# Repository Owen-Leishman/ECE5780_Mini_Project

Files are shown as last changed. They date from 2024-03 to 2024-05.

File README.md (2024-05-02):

# Demonstration Neural Interface
>[!warning]
>This is a demonstration device, this hardware is relatively untested and not gauranteed to be safe! This is not designed live test subjects!

## Overview
This is a demonstration neural interface which is meant to explore how neural interfaces work.  This device can measure four differential signals at a time which can be used to measure nerve impulses and are tolerant of ±9V. It also has a current mode stimulation channel which can create ±1mA signals with 9 bits of resolution as a means to give feedback to the nerves. The stimulation channel can handle electrodes with up to 9kΩ. The device also has a temperature sensor to measure how much it heats up to ensure that it would be safe if implanted (at least temperature wise). The device can be controlled over wifi, and is fully battery powered.

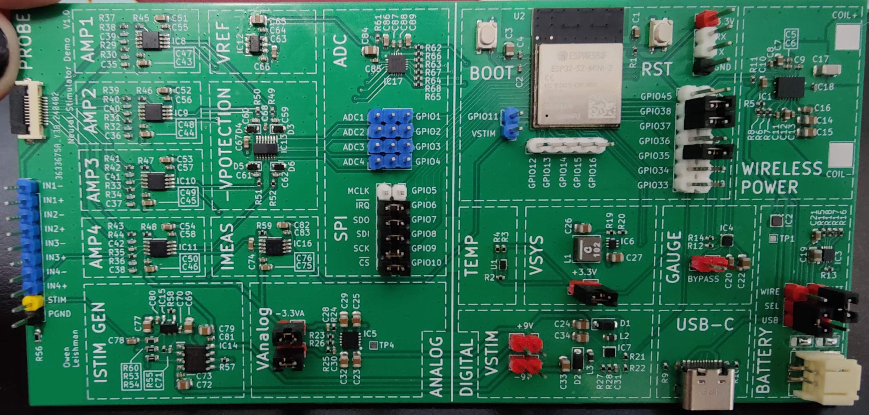
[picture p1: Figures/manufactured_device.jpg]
Manufactured device

(A logo was edited out on the bottom left corner of the device, the photo is otherwise not edited)

## Organization
- [Firmware](/Firmware/Neural_Demo/) contains the code that the device runs.
- [Hardware](/Hardware/) contains the design of the device.
- [Software](/Software/) contains the code used to interface with the device.

For information on how to use the device refer to the [software directory](/Software/).

For information on how to manufacture the device refer to the [hardware directory](/Hardware/).

## Results
The device has exceptional accuracy and can measure down to the uV using its discreate ADC.
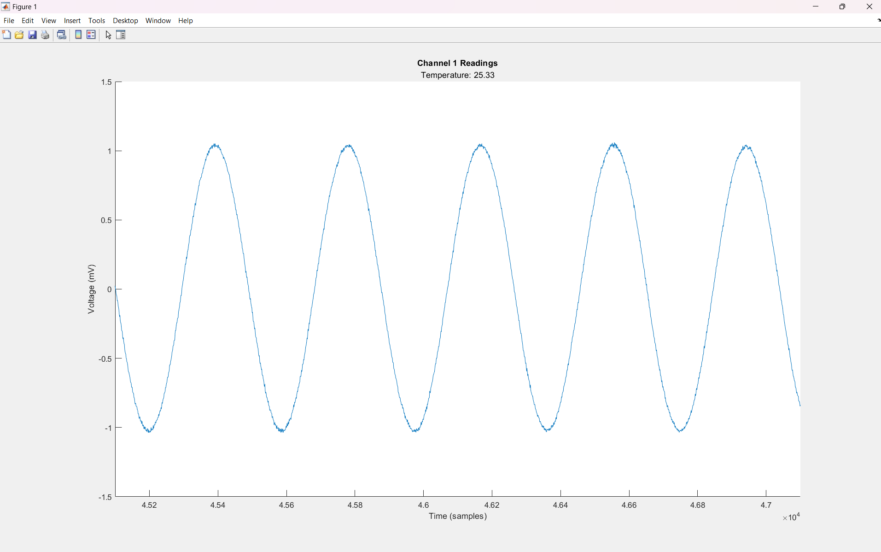
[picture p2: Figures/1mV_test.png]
Low Voltage Test

This test was run using an external signal generator to create a 1mV peak-to-peak sine wave at 500mHz. (This test was also done with old software and firmware some of the ADC configuration has been changed).

The demonstration software makes it possible to measure all four channels in real time over wifi, and the measured stimulation current. The software also makes it possible to control the amplitude and waveform the current stimulation uses.
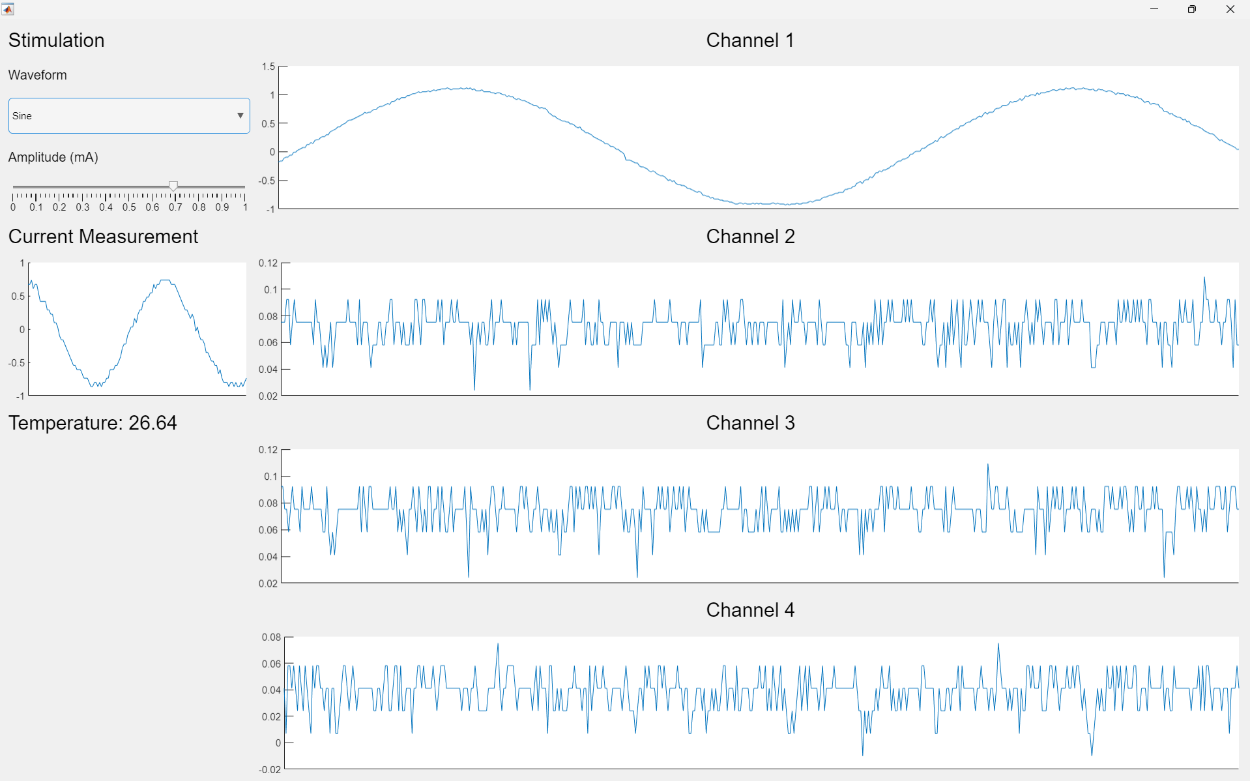
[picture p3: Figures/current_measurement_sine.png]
Full sweet

The discreate ADC broke so the ESP32's onboard ADC (which is much worse) was used for this test. An external signal generator was connected to channel 1 to create a 1V peak-to-peak sine wave, and an external load resistor was used to connect the stimulation output to ground.

# Design Overview
Here are is the top level design of the device, for detailed information on the desing refer to the [hardware directory](Hardware).

## Top Level Design
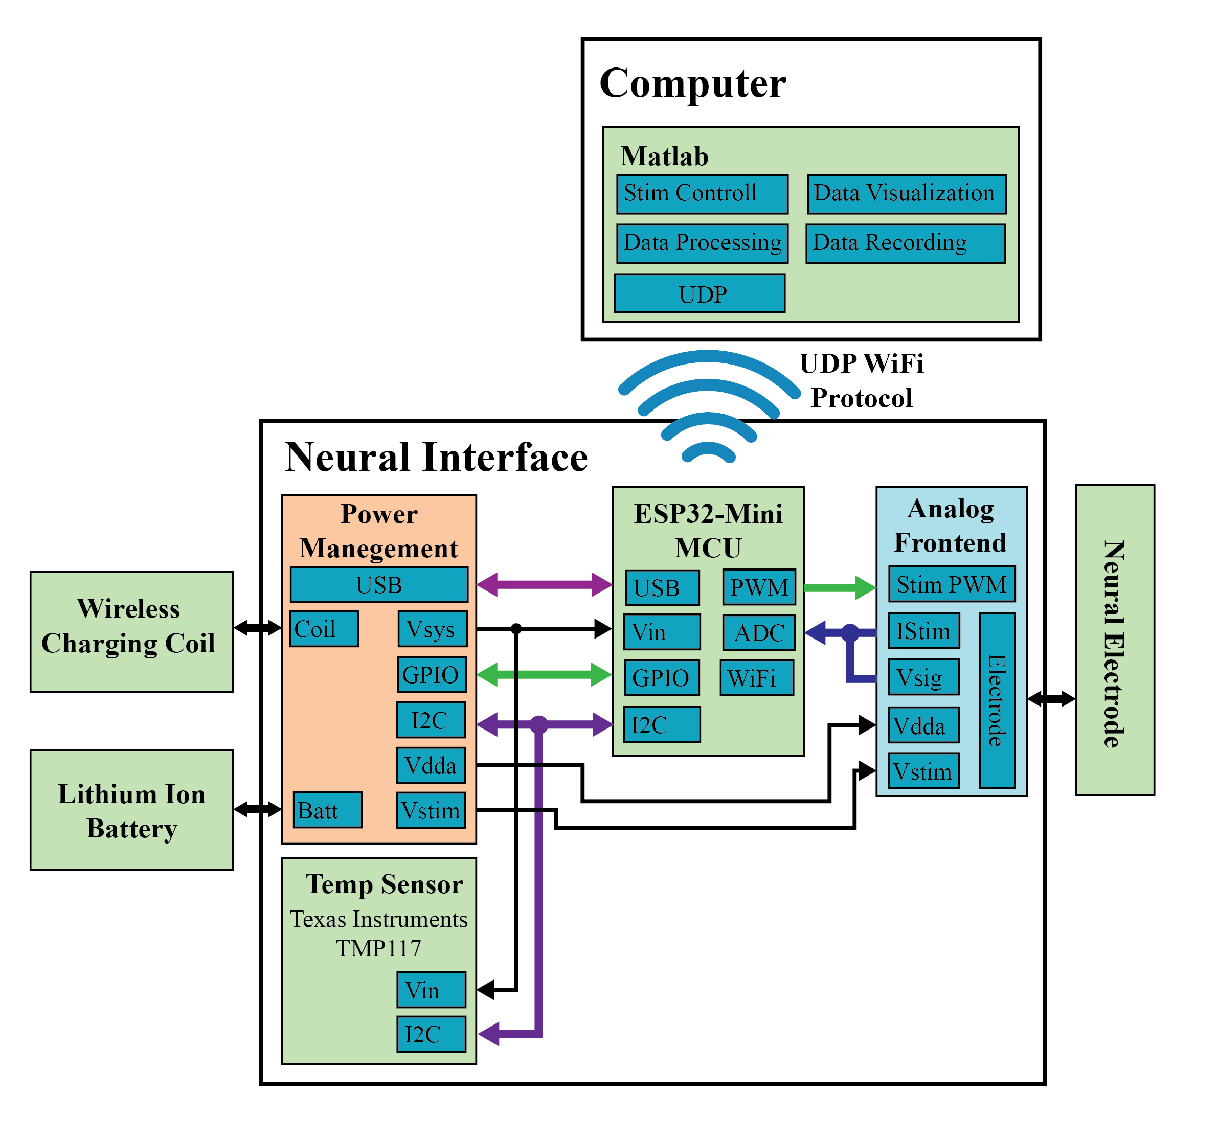
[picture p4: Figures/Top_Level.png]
Top level block diagram

The ESP32 microcontroller is used to control the whole device. The analog frontend is used to aquire data from the differential inputs, and output stimulation signals. The power distrobution block manages the battery and all of the supply voltages.

## Analog Frontend
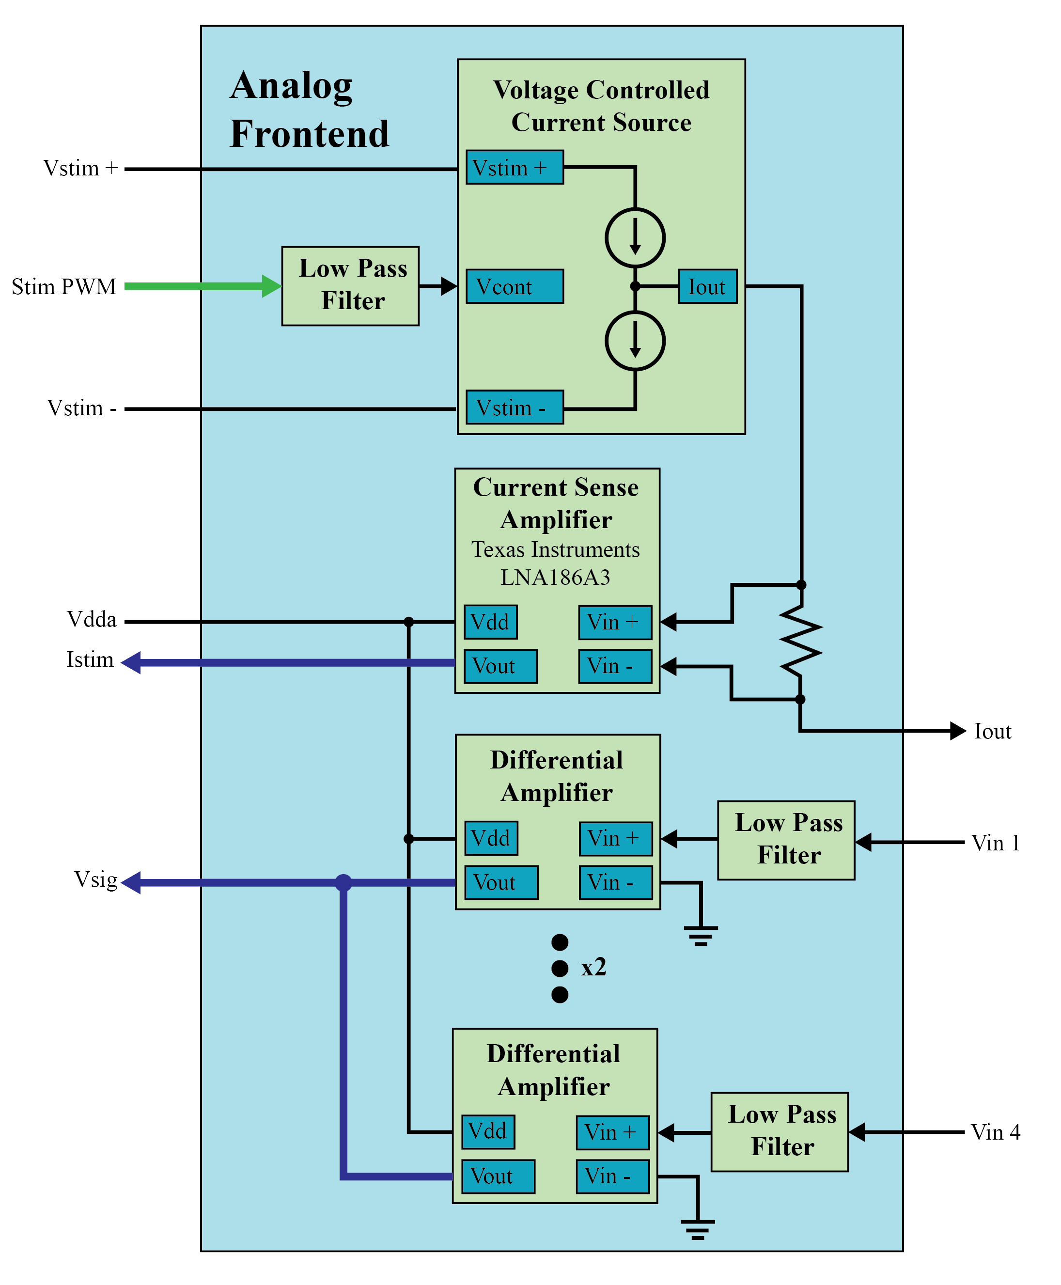
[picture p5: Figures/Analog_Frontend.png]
Analog frontend block diagram


## Power Distrobution
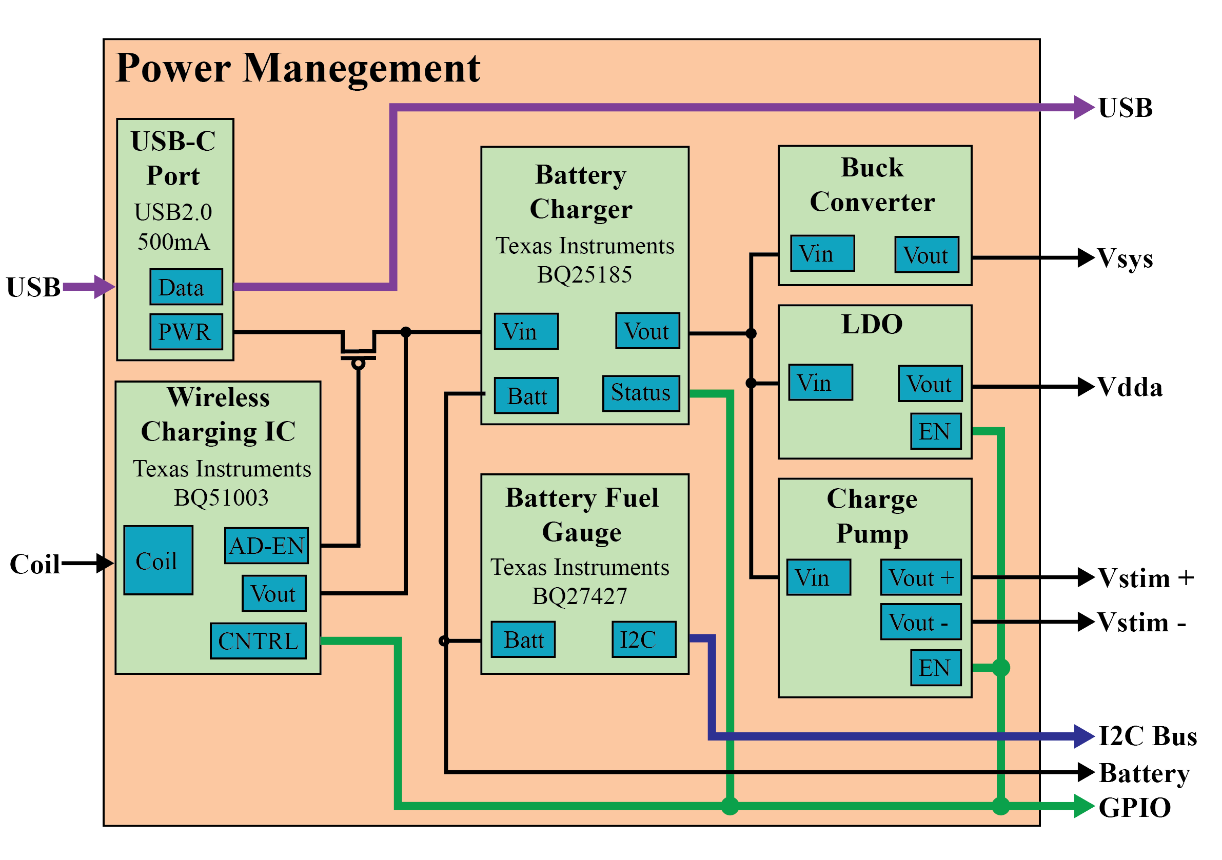
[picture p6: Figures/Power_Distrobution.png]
Power Distrobution block diagram


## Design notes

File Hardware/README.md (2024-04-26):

# Demonstration Neural Interface Hardware
>[!warning]
>This is a demonstration device, this hardware is relatively untested and not gauranteed to be safe! This is not designed live test subjects!

>[!note]
>Made with KiCad version 7.0,  [Kicad Download](https://www.kicad.org/download/)

The hardware for the demonstration neural interface.

## Tasks
- [ ] Test BQ51013BRHLR wirless power IC.
- [ ] Add voltage divider/modify signal path for onboard ADC.
- [ ] Find replacement for AD8067ARTZ operational amplifier used in the current source.
- [ ] Find issues with MCP3464 ADC (may have been ESD)

# Assembled Device
Manufactured device
>[!warning]
>This device uses BGA components and is not trivial to solder. Due to the large amount of surface mount components on the device it is recomended to use a stencil and a reflow oven for soldering.

## Current Source Fix
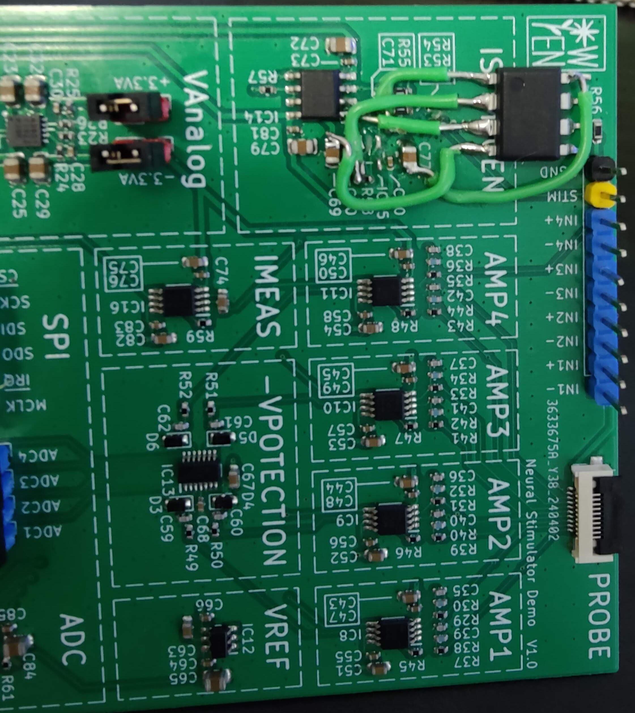
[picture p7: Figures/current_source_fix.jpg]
Current Source Fix

The AD8067ARTZ was broken (reason still unknown) so a LF353N was used to replace it for testing.

## Onboard ADC Fix
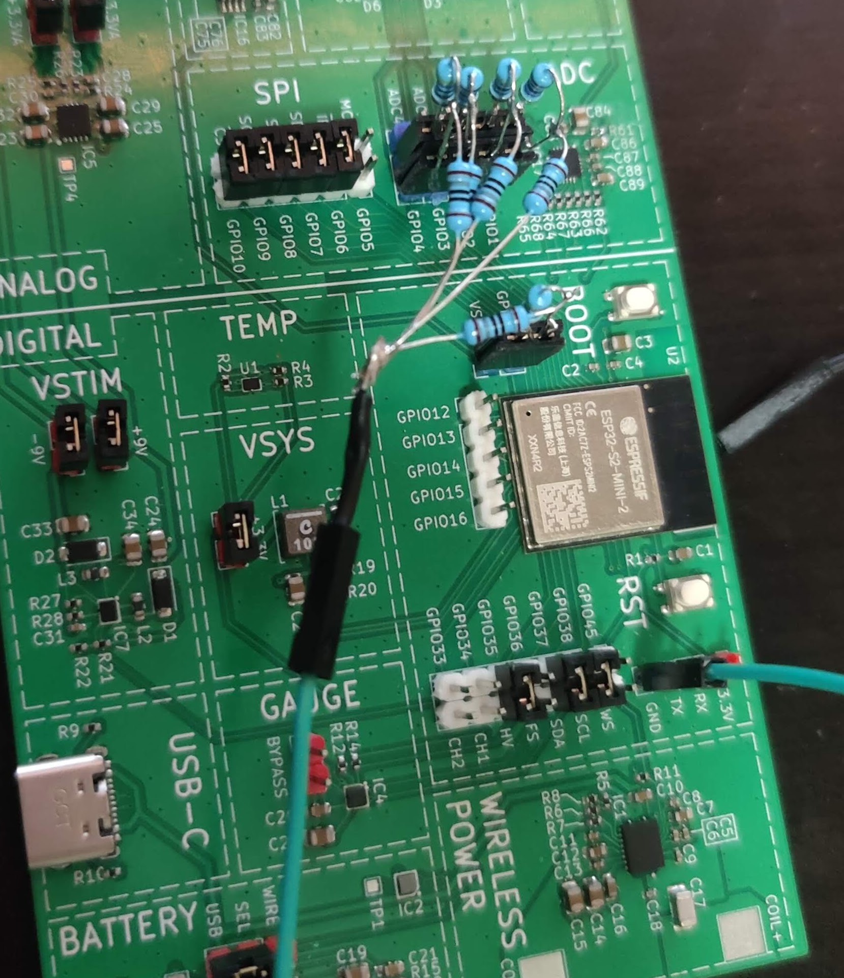
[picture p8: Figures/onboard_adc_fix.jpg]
Onboard ADC Fix

The MCP3464RT ADC broke so the ESP32's onboard ADC was used. The onboard ADC can not measure voltages larger than ~200mV so voltage dividers were added to divide all of the signals into that range, 4.7K and 180R resistors were used to create the voltage dividers. This creates a lot of noise and distortion in the signals. Due to this onboard ADC will not be used or supported in future revisions.

# Schematics
## Top Level Schematic
Top level schematic
Schematic for the ESP32 S2-mini and supporting circuitry which is used to control the device. Jumpers are added between the ESP32's gpio and board signals to make it possible to rerout signals if there is a conflict, or prevent interference for analog signals if the onboard ADC is not being used. The temperature sensor is also on this schematic.

## Analog Frontend Schematic
Analog frontend schematic
Schematic for the analog frontend used to measure "neural" signals and output current mode stimulation. The differential input signals are fed into voltage dividers to ensure that the maximum voltage that reaches the system is ±3.3V, and to create a 1MΩ input impedance. Instrumentation amplifiers are used to amplify the differential signals (satureates at ±1V but is tolerant fo ±9V) and convert them to single ended signals (0-3.3V) centered around Vref (1.6V). The outut of the instrumentation amplifiers is fed into a buffered opamp with a shotkey diode to prevent negative voltages from reaching the ADC when the instrumentation amplifiers get saturated with a negative signal (Ie. an input of -9V), this opamp will likely be removed in future revisions. Low pass filterers and decoupling capacitors are implemented throughout the design to reduce noise.

The current mode stimulation is created using an advanced howland current source implementation based on an [article by Nick Jiang from Analog Devices](https://www.analog.com/en/resources/analog-dialogue/articles/a-large-current-source-with-high-accuracy-and-fast-settling.html). The current sources is controlled by using both DACs on the ESP32, one DAC is used for creating positive currents while the other is used to create negative curents. The maximum output current is ±1mA when 3.3V is supplied by one of the DACs. The maximum probe impedance the current source can handle is 9kΩ, since the stimulation voltage is ±9V. A capacitor is added in series to the output current to prevent continous stimulation in case of a device malfunction (this capacitor was shorted to test the current source at low frequencies).

## Power Manegement Schematic
Power manegement schematic
Schematic for the power manegement circuitry which supplies power to the device and maneges the battery. The device can be powered from using wireless charging, USB type C, or the onboard battery. The BQ51013BRHLR wireless charging IC automatically selects if the BQ25185DLHR battery charging IC will be suplied with usb power or wireless power based on which one is present. The battery charging IC controlls the battery charge rate, and charge and discharge threshold and determines if the voltage regulators for the rest of the system will be supplied with battery power or the power selected by the wireless charging IC. A BQ27427YZFR is placed in series with the battery to measure battery life.

There are three voltage regulators on the device. A buck converter supplies Vsys (+3.3V) to power the ESP32 and TMP117, it is always on when voltage is present. A differential boost converter suplies Vstim (±9V) which poweres the constant current source and is controlled by the ESP32. The rest of the analog frontend is powered with a differential linear dropout regulator (LDO) which is powered from Vstim and reduces the supply noise caused by the switching regulators creating ±3.3V, this is not very effecient and will likely be changed in future revisions. The LDO is always on whenever Vstim is present.

# PCB Layout

>[!note]
>These figures are for reference, there may be some visual issues due to how KiCad exports SVG files.

## Top PCB Layout
Top Layout

## Bottom PCB Layout
Bottom Layout

## 3D Render
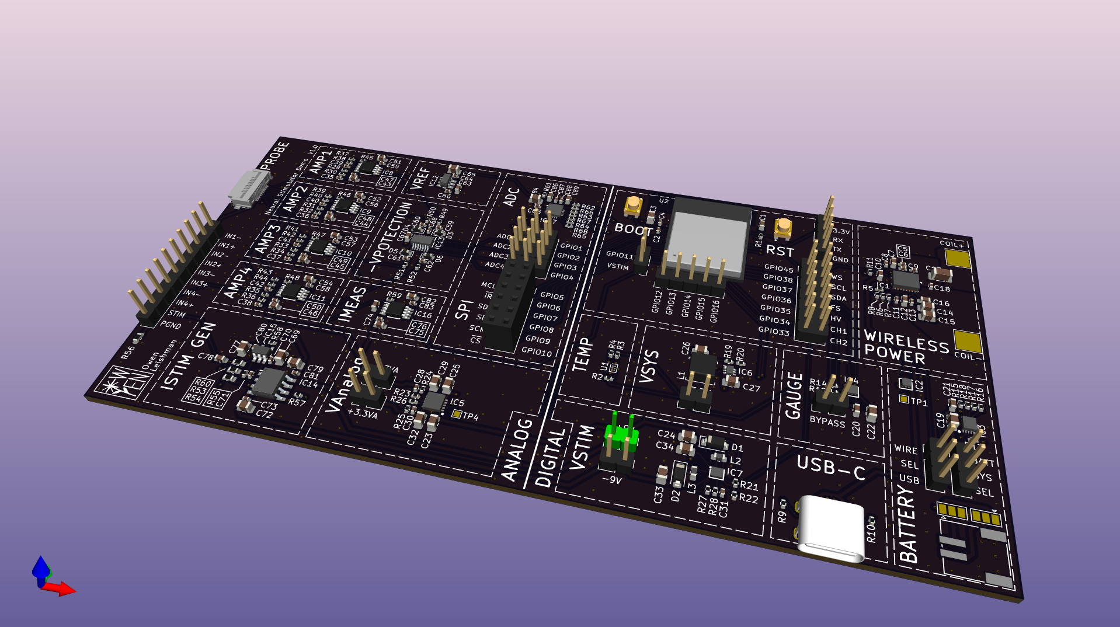
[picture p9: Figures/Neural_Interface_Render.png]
3D render


# Ordering
The design is layed out as a two layer board following [JLC PCB's](https://jlcpcb.com/) constraints, and all components are placed on the top layer. To order zip the [NSD_V1-0](Hardware/NSD_V1-0) directory and submit it to JLC PCB. A stencil can also be ordered from JLC PCB.

All of the parts other than the battery and battery connector can be ordered from [Mouser Electronics](https://www.mouser.com/) and listed [here](Hardware/MouserPartsOrder.xls). The battery and battery connector can be ordered from [DigiKey](https://www.digikey.com/) and are listed [here](Hardware/DigiKeyPartsOrder.xlsx). The [BOM](Hardware/BOM.csv) does not reference passive parts with manufacturer names. Additionaly 2.54mm headers are not included in either of these lists.

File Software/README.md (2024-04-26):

# Demonstration Software

This software is used to give a real-time demonstrate the neural interface. The software connects to the device over wifi and graphs the readings of the device in real time, and allows you to set the current stimulation waveform and amplitude.

Software Example
The channel 1-4 graphs show what voltages the device is measuring over time (in volts). The waveform dropdown selects if the device should output a sine wave or a square wave using the current source, and the amplitude slider selects the amplitude of the stimulation wave in miliamperes. The current measurement graph shows the measured stimulation current over time (in miliamperes).The x-axis of the graphs don't have tick marks to prevent the formating of the graphs to change every time they are updated. The temperature shows the measured temperature in degrees celcius.

This demonstration used a fixed load resistor connected between the current stimulation output and ground, and a signal generator creating a sine wave connected to channel 1. The other channles are left unconnected.

## Usage
>[!note]
>Made with [Matlab](https://www.mathworks.com/products/matlab.html) version 2022a 

To use this software you must have Matlab installed and change the [host IP address](https://github.com/Owen-Leishman/ECE5780_Mini_Project/blob/515b5f4717a34815e817afd9543e5ca668a39d97/Firmware/Neural_Demo/main/udp.c#L21C30-L21C43) in firmware and the [udp IP address](https://github.com/Owen-Leishman/ECE5780_Mini_Project/blob/515b5f4717a34815e817afd9543e5ca668a39d97/Software/neural_ui_udp.m#L6C32-L6C47) in the matlab script to your computers IP address. You must also update the [wifi credentials](https://github.com/Owen-Leishman/ECE5780_Mini_Project/blob/515b5f4717a34815e817afd9543e5ca668a39d97/Firmware/Neural_Demo/main/wifi.c#L16C1-L17C29) in the firmware to allow the device to connect to your router.

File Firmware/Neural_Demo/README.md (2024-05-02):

# Neural Demo Device Firmware

This firmware is written to showcase the basic working principles of the demonstration device such as wifi communication, ADC measurements, temperature measurements, and current mode stimulation. The software used to interface with the device running this firmware can be found [here](Software).

FreeRTOS is used to create tasks to handle Wifi communication.

The ESP32's onboard ADC is used in one-shot mode to measure the actual stimulation current. Since there is a significant amount of noise in these measurements each measurment is an average of 32 readings.

The ESP32's I2C bus is used to communicate to the TMP117 and record temperature data, it is also connected to the BQ27427YZFR which has not been implemented in firmware yet.

The ESP32's SPI bus is used to comunicate to the MCP3464 which is used to measue the output of the analog frontend. The ESP32 uses a edge trigger interupt to read the IRQ line of the MCP3464 to determine if new data is availabe. The MCP3464 is not used for some demonstrations because it broke, the firmware to use the device without the MCP3464 can be found [here](https://github.com/Owen-Leishman/ECE5780_Mini_Project/tree/onboard_ADC) but will not recieve any updates.

This firmware is written for an ESP32 S2 and may not work for other ESP chips.

## Tasks
- [ ] Read the BQ27427YZFR for battery fuel measurements.
- [ ] Read the status of the wireless charger and battery control ICs.
- [ ] Add sleep and low power modes.
- [ ] Fix issue where readings are temporarily stoped when data is recieved over UDP.
- [ ] Measure stimulation accuracy and adjust accordingly.
- [ ] Remove use of floating points in stimulation code.

>[!note]
>Uses ESP IDF version 5.2.1

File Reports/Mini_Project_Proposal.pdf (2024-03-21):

# Demonstration Neural Interface Platform

Owen Leishman
3/8/2024

# Motivation

Neural interfaces are devices that interface directly with the human nervous system by using electrical connections to monitor its activity and provide feedback through stimulation. These devices have a wide range of uses in the medical field from enabling patients with paralysis to communicate, to reducing symptoms for people suffering from neurological conditions such as parkinson’s disease and epilepsy. These devices are complex and heavily regulated making it hard to learn about them.
This project aims to create a simple neural interface capable of recording and stimulating neurons to demonstrate the basic working principles of such devices. The neural interface will be designed to be as safe as possible but will not meet the safety standards necessary for implantation or FDA approval to simplify the design requirements.

# Device Overview

The neural interface will record low level voltages from an electrode (~±0.7V) and transmit its readings over wifi to a computer for visualization and processing and the computer will transmit commands to the neural interface to control its stimulation output. The neural interface will use current controlled stimulation, which applies a constant current through the electrode. Constant current stimulation is desirable over other methods because it deposits a known amount of charge through the electrode. This makes it possible to create a net zero charge in the electrode by alternating positive and negative current stimulations. A buildup of charge in the electrode can be very dangerous as it can cause damage to neurons. The electrode will be made out of a flexible PCB as real neural electrodes are prohibitively expensive for this project. The neural interface will be powered with a lithium-ion battery which can be charged wirelessly or through a USB-C port.
The design of the neural interface is split into three parts, a microcontroller, an analog frontend, and a power management block. An ESP32-S3-Mini was selected for the microcontroller as it is easy to integrate within a system, has an inbuilt wifi transmitter, and contains many peripherals. The ESP32 will use its GPIO pins and an I2C bus to control the power management block. The ESP32 will use PWM to control the stimulation output, and use its ADCs to record electrode voltages from the analog frontend. The analog frontend will use an enhanced howland current source controlled using PWM to create the stimulation current, with a shunt resistor and current sense amplifier to provide feedback to the microcontroller. The analog frontend also includes amplifiers to shift the differential input voltage (~±0.7V) to a unipolar voltage (0 - 3.3V) that the ESP32’s ADCs can read. The constant current source requires a large differential voltage (~±10V) and the amplifier requires a smaller differential voltage (~3.3V) both of which will be provided by the power management block.
The power management block uses a battery charger chip to interface with a lithium-ion battery, this makes it possible to safely charge the battery and prevent the battery from over discharging. A battery fuel gauge is used to allow the microcontroller to easily read how much energy is left in the battery. A wireless charging chip allows the device to be charged using a wireless charger. Various voltage regulator chips are used to create the different voltages needed by the system, these will be chosen according to the noise and power requirements of each power domain. The power management unit is complex, but the wireless charging and fuel gauge components are not necessary for it to work, if the unit proves too difficult the device can be powered externally using a power supply.

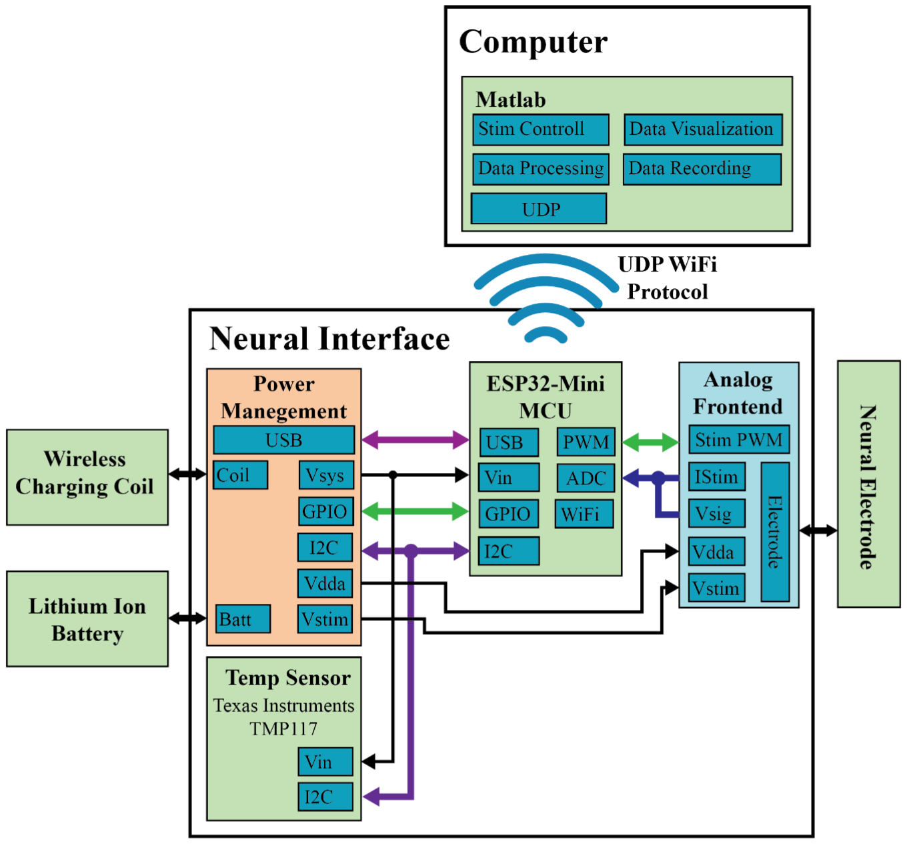
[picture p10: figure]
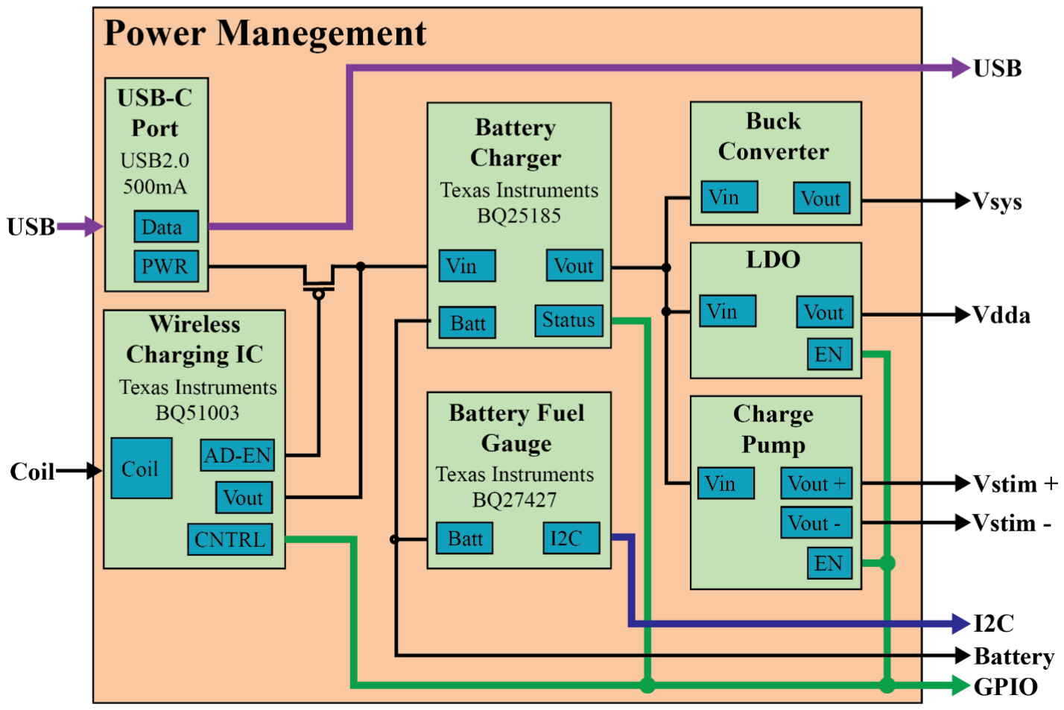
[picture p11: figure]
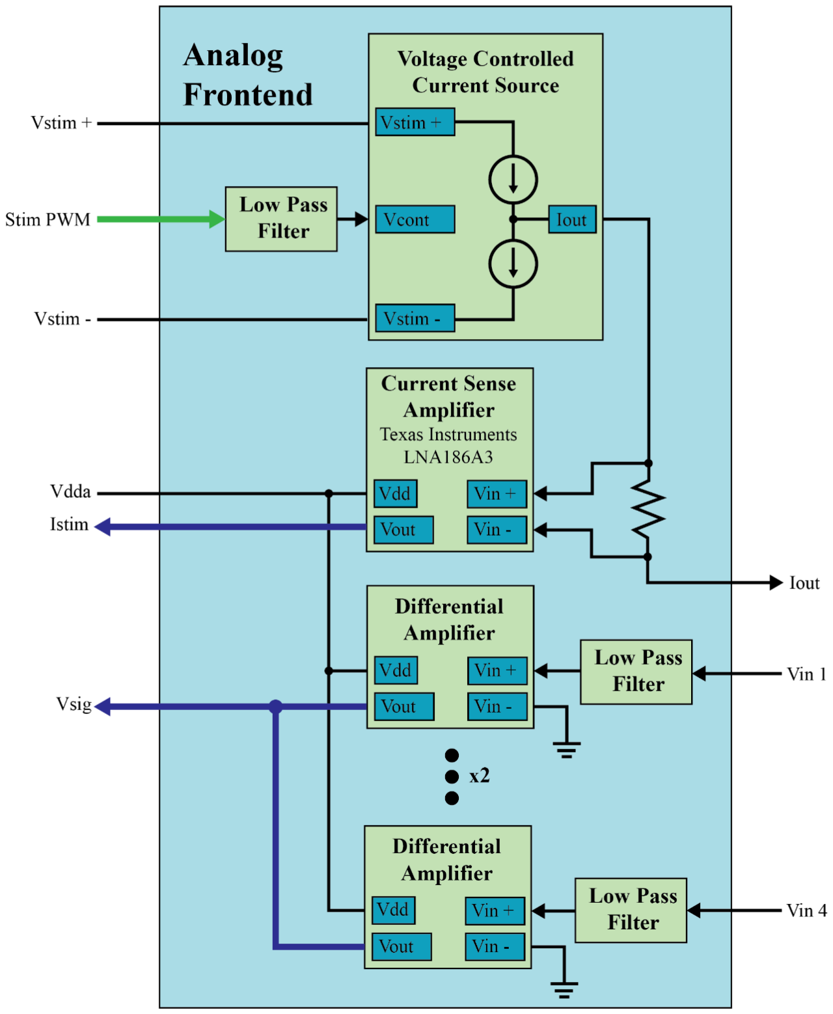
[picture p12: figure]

# Milestones

- Milestone 1: Assemble the device. order components, design and order a PCB, and solder it.
- Milestone 2: Program each subsystem to ensure functionality. Be able to use the ESP32’s WiFi, PWM, GPIO, and ADC peripherals. Ensure that the analog front end and power management block work.
- Milestone 3: Integrate all of the subsystems. The ESP32 reads the values from the ADCs and transmits them over WiFi, and can control the stimulation and power management block.

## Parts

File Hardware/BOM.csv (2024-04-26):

Item | Qty | Reference(s) | Value | LibPart | Footprint | Datasheet | DNP | Height | Manufacturer_Name | Manufacturer_Part_Number | Mouser Part Number | Mouser Price/Stock
1 | 21 | C1, C10, C16, C20, C21, C43, C44, C45, C46, C51, C52, C53, C54, C63, C67, C74, C75, C78, C82, C86, C89 | 1u | Device:C | Capacitor_SMD:C_0603_1608Metric | ~
2 | 24 | C2, C4, C5, C31, C47, C48, C49, C50, C55, C56, C57, C58, C64, C66, C68, C70, C73, C76, C80, C81, C83, C85, C87, C88 | 100n | Device:C | Capacitor_SMD:C_0402_1005Metric | ~
3 | 20 | C3, C14, C15, C19, C22, C23, C24, C25, C26, C27, C29, C32, C33, C34, C65, C69, C72, C77, C79, C84 | 10u | Device:C | Capacitor_SMD:C_0805_2012Metric | ~
4 | 5 | C6, C9, C13, C28, C30 | 10n | Device:C | Capacitor_SMD:C_0402_1005Metric | ~
5 | 2 | C7, C12 | 470n | Device:C | Capacitor_SMD:C_0603_1608Metric | ~
6 | 2 | C8, C11 | 47n | Device:C | Capacitor_SMD:C_0402_1005Metric | ~
7 | 1 | C17 | 82n | Device:C | Capacitor_SMD:C_1206_3216Metric | ~
8 | 1 | C18 | 820p | Device:C | Capacitor_SMD:C_0402_1005Metric | ~
9 | 12 | C35, C36, C37, C38, C39, C40, C41, C42, C59, C60, C61, C62 | 30p | Device:C | Capacitor_SMD:C_0402_1005Metric | ~
10 | 1 | C71 | 200p | Device:C | Capacitor_SMD:C_0402_1005Metric | ~
11 | 2 | D1, D2 | MBR130T1G | Device:D_Schottky | Diode_SMD:D_SOD-123 | https://www.mouser.com/datasheet/2/308/1/MBR130T1_D-2315168.pdf
12 | 4 | D3, D4, D5, D6 | CDBU0130L-HF | Device:D_Schottky | Diode_SMD:D_0603_1608Metric | https://www.mouser.com/datasheet/2/308/1/MBR130T1_D-2315168.pdf
13 | 1 | IC1 | BQ51013BRHLR | Neural_Components:BQ51013BRHLR | Neural_Footprints:BQ51050BRHLR | http://www.ti.com/lit/ds/symlink/bq51013b.pdf |  |  | Texas Instruments | BQ51013BRHLR | 595-BQ51013BRHLR | https://www.mouser.co.uk/ProductDetail/Texas-Instruments/BQ51013BRHLR?qs=y1vSg4rOnUJlN8ZPg6D5Pw%3D%3D
14 | 1 | IC2 | CSD75207W15 | Neural_Components:CSD75207W15 | Neural_Footprints:BGA9C50P3X3_146X146X62 |  |  | 0.62 | Texas Instruments | CSD75207W15 | 595-CSD75207W15 | https://www.mouser.co.uk/ProductDetail/Texas-Instruments/CSD75207W15?qs=7GxONfNUZSic02Y%252BL1RXkQ%3D%3D
15 | 1 | IC3 | BQ25185DLHR | Neural_Components:BQ25185DLHR | Neural_Footprints:SON40P220X200X80-11N | https://www.ti.com/lit/ds/symlink/bq25185.pdf?ts=1706857561339 |  | 0.8 | Texas Instruments | BQ25185DLHR | 595-BQ25185DLHR | https://www.mouser.co.uk/ProductDetail/Texas-Instruments/BQ25185DLHR?qs=Z%252BL2brAPG1IbO%2FV3RqsaPw%3D%3D
16 | 1 | IC4 | BQ27427YZFR | Neural_Components:BQ27427YZFR | Neural_Footprints:BGA9C50P3X3_158X162X62 | https://www.ti.com/lit/ds/symlink/bq27427.pdf?ts=1687698267991 |  | 0.625 | Texas Instruments | BQ27427YZFR | 595-BQ27427YZFR | https://www.mouser.co.uk/ProductDetail/Texas-Instruments/BQ27427YZFR?qs=rQFj71Wb1eU5v%2FHj43hVJQ%3D%3D
17 | 1 | IC5 | TPS7A3901DSCR | Neural_Components:TPS7A3901DSCR | Neural_Footprints:SON50P300X300X80-11N-D | http://www.ti.com/lit/gpn/tps7a39 |  | 0.8 | Texas Instruments | TPS7A3901DSCR | 595-TPS7A3901DSCR | https://www.mouser.co.uk/ProductDetail/Texas-Instruments/TPS7A3901DSCR?qs=BZBei1rCqCCul7wIRif5AQ%3D%3D
18 | 1 | IC6 | TLV62585DRLR | Neural_Components:TLV62585DRLR | Neural_Footprints:SOTFL50P160X60-6N | http://www.ti.com/lit/gpn/tlv62585 |  | 0.6 | Texas Instruments | TLV62585DRLR | 595-TLV62585DRLR | https://www.mouser.co.uk/ProductDetail/Texas-Instruments/TLV62585DRLR?qs=F5EMLAvA7IB9kT1Dd5uf2g%3D%3D
19 | 1 | IC7 | BD8316GWL-E2 | Neural_Components:BD8316GWL-E2 | Neural_Footprints:BGA11C40P4X3_180X150X55 | https://fscdn.rohm.com/en/products/databook/datasheet/ic/power/switching_regulator/bd8316gwl-e.pdf |  | 0.55 | ROHM Semiconductor | BD8316GWL-E2 | 755-BD8316GWL-E2 | https://www.mouser.co.uk/ProductDetail/ROHM-Semiconductor/BD8316GWL-E2?qs=9Cg39qEKpi4sbGytSKsU5Q%3D%3D
20 | 5 | IC8, IC9, IC10, IC11, IC16 | INA823DGKR | Neural_Components:INA823DGKR | Neural_Footprints:SOP65P490X110-8N | https://www.ti.com/lit/ds/symlink/ina823.pdf?ts=1710405274655 |  | 1.1 | Texas Instruments | INA823DGKR | 595-INA823DGKR | https://www.mouser.co.uk/ProductDetail/Texas-Instruments/INA823DGKR?qs=Rp5uXu7WBW%252BTcPLLKQJgaw%3D%3D
21 | 1 | IC12 | REF35160QDBVR | Neural_Components:REF35160QDBVR | Neural_Footprints:SOT95P280X145-6N | https://www.ti.com/lit/ds/symlink/ref35.pdf?ts=1675771464754 |  | 1.45 | Texas Instruments | REF35160QDBVR | 595-REF35160QDBVR | https://www.mouser.co.uk/ProductDetail/Texas-Instruments/REF35160QDBVR?qs=rQFj71Wb1eVJh8regkgQhg%3D%3D
22 | 1 | IC13 | LM324LVIDYYR | Neural_Components:LM324LVIDYYR | Neural_Footprints:SOP50P326X110-14N | https://www.ti.com/lit/ds/symlink/lm358lv.pdf?HQS=dis-mous-null-mousermode-dsf-pf-null-wwe&ts=1695894494145 |  | 1.1 | Texas Instruments | LM324LVIDYYR | 595-LM324LVIDYYR | https://www.mouser.co.uk/ProductDetail/Texas-Instruments/LM324LVIDYYR?qs=MyNHzdoqoQIMQL6h%252B3q%252Baw%3D%3D
23 | 1 | IC14 | ADA4898-2YRDZ | Neural_Components:ADA4898-2YRDZ | Neural_Footprints:SOIC127P600X175-9N | https://www.analog.com/media/en/technical-documentation/data-sheets/ADA4898-1_4898-2.pdf |  | 1.75 | Analog Devices | ADA4898-2YRDZ | 584-ADA4898-2YRDZ | https://www.mouser.co.uk/ProductDetail/Analog-Devices/ADA4898-2YRDZ?qs=BpaRKvA4VqGTtFNzXN87wQ%3D%3D
24 | 1 | IC15 | AD8067ARTZ-REEL7 | Neural_Components:AD8067ARTZ-REEL7 | Neural_Footprints:SOT95P280X145-5N |  |  |  | Analog Devices | AD8067ARTZ-REEL7 | 584-AD8067ARTZ-R7 | https://www.mouser.co.uk/ProductDetail/Analog-Devices/AD8067ARTZ-REEL7?qs=%2FtpEQrCGXCxI5tNv%252B6Ufew%3D%3D
25 | 1 | IC17 | MCP3464RT-E_NC | Neural_Components:MCP3464RT-E_NC | Neural_Footprints:QFN40P300X300X60-21N-D | https://componentsearchengine.com/Datasheets/2/MCP3464RT-E_NC.pdf |  | 0.6 | Microchip | MCP3464RT-E/NC | 579-MCP3464RT-E/NC | https://www.mouser.co.uk/ProductDetail/Microchip-Technology/MCP3464RT-E-NC?qs=W%2FMpXkg%252BdQ5Ehc3kIRQ52g%3D%3D
26 | 1 | J1 | Conn_02x07_Odd_Even | Connector_Generic:Conn_02x07_Odd_Even | Connector_PinHeader_2.54mm:PinHeader_2x07_P2.54mm_Vertical | ~
27 | 1 | J2 | Conn_02x06_Odd_Even | Connector_Generic:Conn_02x06_Odd_Even | Connector_PinSocket_2.54mm:PinSocket_2x06_P2.54mm_Vertical | ~
28 | 1 | J3 | Conn_01x05 | Connector_Generic:Conn_01x05 | Connector_PinHeader_2.54mm:PinHeader_1x05_P2.54mm_Vertical | ~
29 | 1 | J4 | Conn_01x04 | Connector_Generic:Conn_01x04 | Connector_PinHeader_2.54mm:PinHeader_1x04_P2.54mm_Vertical | ~
30 | 6 | J5, J10, J18, J19, J20, J21 | Conn_01x03 | Connector_Generic:Conn_01x03 | Connector_PinHeader_2.54mm:PinHeader_1x03_P2.54mm_Vertical | ~
31 | 7 | J6, J11, J12, J13, J14, J15, J22 | Conn_01x02 | Connector_Generic:Conn_01x02 | Connector_PinHeader_2.54mm:PinHeader_1x02_P2.54mm_Vertical | ~
32 | 1 | J7 | S2B-PH-SM4-TB | Neural_Components:S2B-PH-SM4-TB | Neural_Footprints:CONN_S2B-PH-SM4-TB_JST | S2B-PH-SM4-TB
33 | 2 | J8, J9 | Conn_01x03 | Connector_Generic:Conn_01x03 | Jumper:SolderJumper-3_P1.3mm_Open_Pad1.0x1.5mm | ~
34 | 1 | J16 | Conn_01x10 | Connector_Generic:Conn_01x10 | Connector_PinHeader_2.54mm:PinHeader_1x10_P2.54mm_Vertical | ~
35 | 1 | J17 | 505110-1092 | Neural_Components:505110-1092 | Neural_Footprints:5051101092 | https://www.molex.com/webdocs/datasheets/pdf/en-us/5051101092_FFC_FPC_CONNECTORS.pdf |  | 0 | Molex | 505110-1092 | 538-505110-1092 | https://www.mouser.co.uk/ProductDetail/Molex/505110-1092?qs=BA62vJVifGrjJfo6A8tlOw%3D%3D
36 | 1 | L1 | 1uH | Device:L | Inductor_SMD:L_Coilcraft_XAL4020-XXX | https://www.mouser.com/ProductDetail/Coilcraft/XFL4020-102MEC?qs=zCSbvcPd3pbaYHL7viZwQA%3D%3D
37 | 2 | L2, L3 | 4.7uH | Device:L | Inductor_SMD:L_0603_1608Metric | https://www.mouser.com/datasheet/2/281/1/JELF243B_0033-1634182.pdf
38 | 19 | R1, R2, R3, R4, R8, R11, R12, R13, R14, R15, R16, R22, R23, R26, R28, R49, R50, R51, R52 | 10k | Device:R | Resistor_SMD:R_0402_1005Metric | ~
39 | 1 | R5 | 330 | Device:R | Resistor_SMD:R_0402_1005Metric | ~
40 | 1 | R6 | 196 | Device:R | Resistor_SMD:R_0402_1005Metric | ~
41 | 1 | R7 | 20k | Device:R | Resistor_SMD:R_0402_1005Metric | ~
42 | 2 | R9, R10 | 5.1k | Device:R | Resistor_SMD:R_0402_1005Metric | ~
43 | 1 | R17 | 130k | Device:R | Resistor_SMD:R_0402_1005Metric | ~
44 | 1 | R18 | 3k | Device:R | Resistor_SMD:R_0402_1005Metric | ~
45 | 1 | R19 | 453k | Device:R | Resistor_SMD:R_0402_1005Metric | ~
46 | 2 | R20, R21 | 100k | Device:R | Resistor_SMD:R_0402_1005Metric | ~
47 | 1 | R24 | 28k | Device:R | Resistor_SMD:R_0402_1005Metric | ~
48 | 1 | R25 | 17.8k | Device:R | Resistor_SMD:R_0402_1005Metric | ~
49 | 1 | R27 | 90.9k | Device:R | Resistor_SMD:R_0402_1005Metric | ~
50 | 8 | R29, R31, R33, R35, R37, R39, R41, R43 | 600k | Device:R | Resistor_SMD:R_0402_1005Metric | ~
51 | 8 | R30, R32, R34, R36, R38, R40, R42, R44 | 332k | Device:R | Resistor_SMD:R_0402_1005Metric | ~
52 | 4 | R45, R46, R47, R48 | 24.9k | Device:R | Resistor_SMD:R_0402_1005Metric | ~
53 | 2 | R53, R54 | 82.5k | Device:R | Resistor_SMD:R_0603_1608Metric | ~
54 | 2 | R55, R57 | 100R | Device:R | Resistor_SMD:R_0402_1005Metric | ~
55 | 1 | R56 | 1R | Device:R | Resistor_SMD:R_0603_1608Metric | ~
56 | 1 | R58 | 2k | Device:R | Resistor_SMD:R_0402_1005Metric | ~
57 | 1 | R59 | 200 | Device:R | Resistor_SMD:R_0402_1005Metric | ~
58 | 1 | R60 | 4R | Device:R | Resistor_SMD:R_0603_1608Metric | ~
59 | 8 | R61, R62, R63, R64, R65, R66, R67, R68 | 10R | Device:R | Resistor_SMD:R_0402_1005Metric | ~
60 | 1 | SW1 | RESET | Switch:SW_Push | ASIC_Implementation_Library:PTS815SJM250SMTRLFS | ~
61 | 1 | SW2 | BOOT | Switch:SW_Push | ASIC_Implementation_Library:PTS815SJM250SMTRLFS | ~
62 | 2 | TP1, TP4 | TestPoint | Connector:TestPoint | TestPoint:TestPoint_Pad_1.0x1.0mm | ~
63 | 2 | TP2, TP3 | TestPoint | Connector:TestPoint | TestPoint:TestPoint_Pad_4.0x4.0mm | ~
64 | 1 | U1 | TMP117 | Motor_Driver:TMP117 | Package_BGA:Texas_DSBGA-6_0.95x1.488mm_Layout2x3_P0.4mm | https://www.ti.com/lit/ds/symlink/tmp117.pdf?ts=1705219508033
65 | 1 | U2 | ~ | ASIC_Implementation:ESP32-S2-mini-1 | ASIC_Implementation_Library:ESP32S2MINI1N4R2
66 | 1 | U3 | USB4105 | USBC:USB4105 | ASIC_Implementation_Library:USB4105 | https://www.mouser.com/datasheet/2/837/usb4105-2448855.pdf

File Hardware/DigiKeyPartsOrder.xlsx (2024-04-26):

Country of Origin may be different at time of shipment.
The HTSUS and ECCN information shown is for informational purposes only and is not a representation or warranty as to the accuracy or reliability of these classifications. All information is provided "as is" and is subject to change without notice. Any use made of the information provided is without recourse to Digi-Key and at the user's risk.
Index | Manufacturer Part Number | Manufacturer Name | Description | Availability | Stock Status | Attrition % | Requested Quantity 1 | Pack Quantity 1 | Pack Type 1 | Digi-Key Part Number 1 | Unit Price 1 | Extended Price 1 | Minimum Order Quantity 1 | Customer Reference | Requested Part Number | Lead Weeks | Datasheet | Reference Designator | US Import Tariff | Note | Part Status | RoHS Status | Moisture Sensitivity Level (MSL) | ECCN | HTSUS | Country of Origin | Environmental Information | Original Part numbers | Image | Product Notes
1 | S2B-PH-SM4-TB | JST Sales America Inc. | CONN HEADER SMD R/A 2POS 2MM | 177,567 | In Stock |  | 1 | 1 | Cut Tape (CT) | 455-S2B-PH-SM4-TBCT-ND | 0.58000 | $0.58 | 1 |  | 455-S2B-PH-SM4-TBCT-ND | 16 | https://www.jst-mfg.com/product/pdf/eng/ePH.pdf |  | N/A |  | Active | ROHS3 Compliant | 1 (Unlimited) | EAR99 | 8536.69.4040 | Malaysia |  | 455-S2B-PH-SM4-TBCT-ND | https://mm.digikey.com/Volume0/opasdata/d220001/medias/images/1117/S2B-PH-SM3-TB.jpg
2 | PRT-13851 | SparkFun Electronics | BATTERY LITH-ION 3.7V 400MAH | 376 | In Stock |  | 1 | 1 | Bulk | 1568-1493-ND | 5.50000 | $5.50 | 1 |  | 1568-1493-ND | 5 | https://cdn.sparkfun.com/datasheets/Prototyping/spe-00-502535-400mah-en-1.0ver.pdf |  | N/A |  | Active | ROHS3 Compliant | Not Applicable | EAR99 | 8507.60.0020 | China |  | 1568-1493-ND | https://mm.digikey.com/Volume0/opasdata/d220001/medias/images/2169/MFG_PRT-13851.jpg
3 | AD844JRZ-16-REEL7 | Analog Devices Inc. | IC OPAMP CFA 1 CIRCUIT 16SOIC | 351 | In Stock |  |  |  |  |  |  |  |  |  | 505-AD844JRZ-16-REEL7CT-ND | 10 | https://www.analog.com/media/en/technical-documentation/data-sheets/AD844.pdf |  | N/A |  | Active | ROHS3 Compliant | 1 (Unlimited) | EAR99 | 8542.33.0001 | Taiwan |  | 505-AD844JRZ-16-REEL7CT-ND | https://mm.digikey.com/Volume0/opasdata/d220001/medias/images/4295/505%7ERW-16%7ERW%7E16.jpg

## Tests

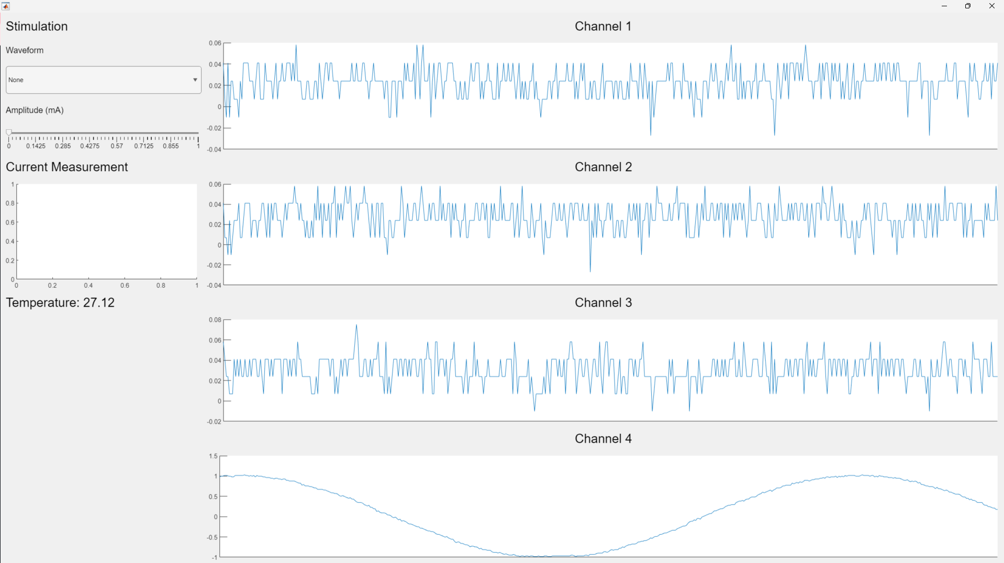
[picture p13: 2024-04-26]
Figures/onboard_adc_test.png

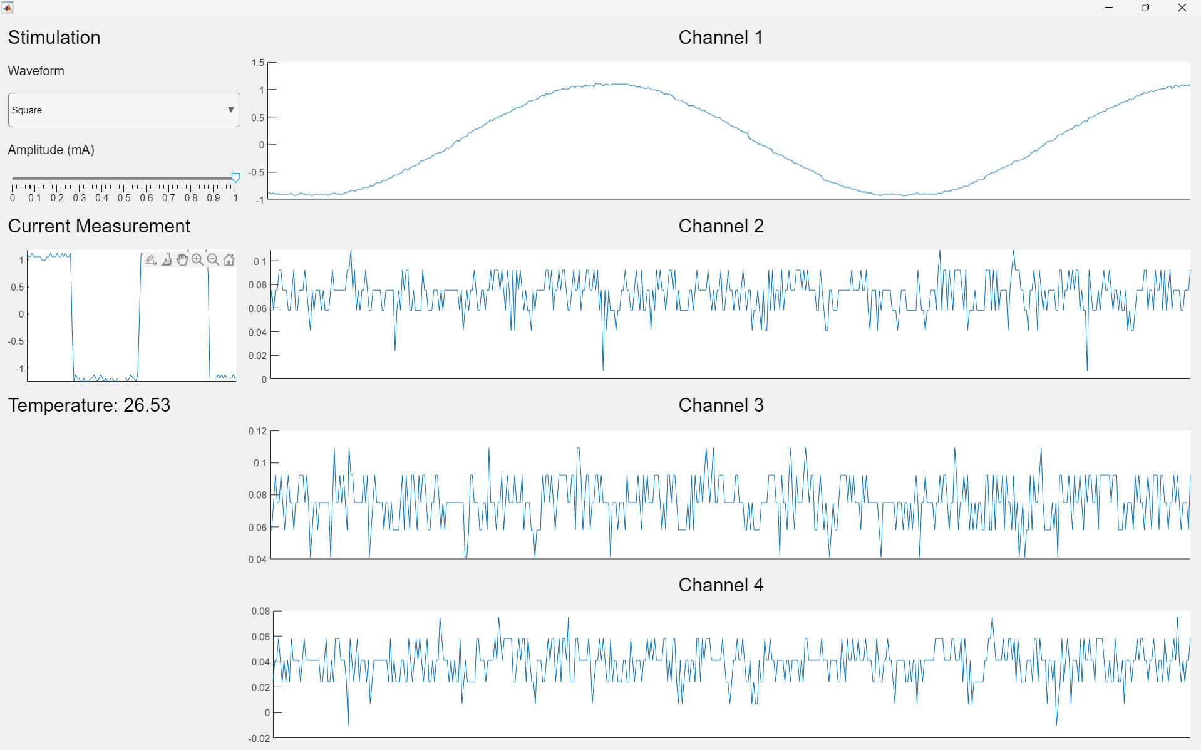
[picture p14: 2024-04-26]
Figures/current_measurement_square.png

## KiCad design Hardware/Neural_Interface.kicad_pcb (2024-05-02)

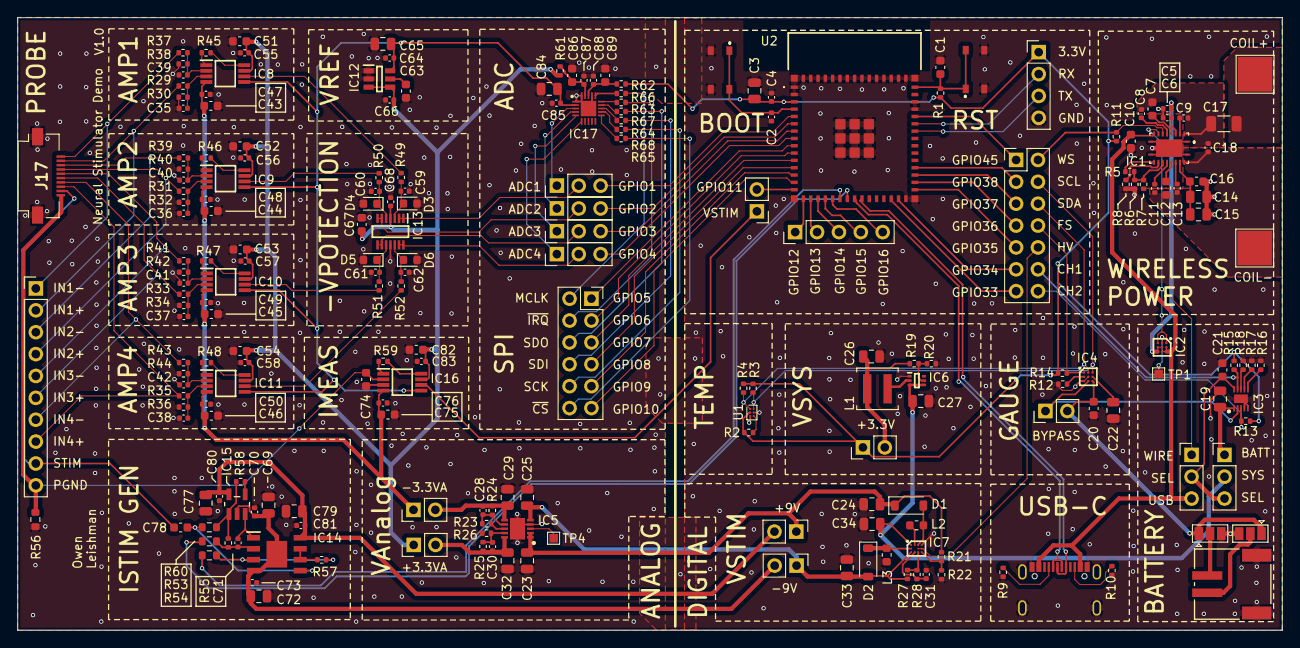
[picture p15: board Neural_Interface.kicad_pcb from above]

Board: 2 copper layers, 146.9 x 71.1 mm, 214 parts (0 on the bottom side), 161 nets.

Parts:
C1, C10, C16, C20, C21, C43, C44, C45, C46, C51, C52, C53, C54, C63, C67, C74, C75, C78, C82, C86, C89: 1u; C_0603_1608Metric
C2, C4, C5, C31, C47, C48, C49, C50, C55, C56, C57, C58, C64, C66, C68, C70, C73, C76, C80, C81, C83, C85, C87, C88: 100n; C_0402_1005Metric
C3, C14, C15, C19, C22, C23, C24, C25, C26, C27, C29, C32, C33, C34, C65, C69, C72, C77, C79, C84: 10u; C_0805_2012Metric
C6, C9, C13, C28, C30: 10n; C_0402_1005Metric
C7, C12: 470n; C_0603_1608Metric
C8, C11: 47n; C_0402_1005Metric
C17: 82n; C_1206_3216Metric
C18: 820p; C_0402_1005Metric
C35, C36, C37, C38, C39, C40, C41, C42, C59, C60, C61, C62: 30p; C_0402_1005Metric
C71: 200p; C_0402_1005Metric
D1, D2: MBR130T1G; D_SOD-123
D3, D4, D5, D6: CDBU0130L-HF; D_0603_1608Metric
IC1: BQ51013BRHLR; BQ51050BRHLR
IC2: CSD75207W15; BGA9C50P3X3_146X146X62
IC3: BQ25185DLHR; SON40P220X200X80-11N
IC4: BQ27427YZFR; BGA9C50P3X3_158X162X62
IC5: TPS7A3901DSCR; SON50P300X300X80-11N-D
IC6: TLV62585DRLR; SOTFL50P160X60-6N
IC7: BD8316GWL-E2; BGA11C40P4X3_180X150X55
IC8, IC9, IC10, IC11, IC16: INA823DGKR; SOP65P490X110-8N
IC12: REF35160QDBVR; SOT95P280X145-6N
IC13: LM324LVIDYYR; SOP50P326X110-14N
IC14: ADA4898-2YRDZ; SOIC127P600X175-9N
IC15: AD8067ARTZ-REEL7; SOT95P280X145-5N
IC17: MCP3464RT-E_NC; QFN40P300X300X60-21N-D
J1: Conn_02x07_Odd_Even; PinHeader_2x07_P2.54mm_Vertical
J2: Conn_02x06_Odd_Even; PinSocket_2x06_P2.54mm_Vertical
J3: Conn_01x05; PinHeader_1x05_P2.54mm_Vertical
J4: Conn_01x04; PinHeader_1x04_P2.54mm_Vertical
J5, J10, J18, J19, J20, J21: Conn_01x03; PinHeader_1x03_P2.54mm_Vertical
J6, J11, J12, J13, J14, J15, J22: Conn_01x02; PinHeader_1x02_P2.54mm_Vertical
J7: S2B-PH-SM4-TB; CONN_S2B-PH-SM4-TB_JST
J8, J9: Conn_01x03; SolderJumper-3_P1.3mm_Open_Pad1.0x1.5mm
J16: Conn_01x10; PinHeader_1x10_P2.54mm_Vertical
J17: 505110-1092; 5051101092
L1: 1uH; L_Coilcraft_XAL4020-XXX
L2, L3: 4.7uH; L_0603_1608Metric
R1, R2, R3, R4, R8, R11, R12, R13, R14, R15, R16, R22, R23, R26, R28, R49, R50, R51, R52: 10k; R_0402_1005Metric
R5: 330; R_0402_1005Metric
R6: 196; R_0402_1005Metric
R7: 20k; R_0402_1005Metric
R9, R10: 5.1k; R_0402_1005Metric
R17: 130k; R_0402_1005Metric
R18: 3k; R_0402_1005Metric
R19: 453k; R_0402_1005Metric
R20, R21: 100k; R_0402_1005Metric
R24: 28k; R_0402_1005Metric
R25: 17.8k; R_0402_1005Metric
R27: 90.9k; R_0402_1005Metric
R29, R31, R33, R35, R37, R39, R41, R43: 600k; R_0402_1005Metric
R30, R32, R34, R36, R38, R40, R42, R44: 332k; R_0402_1005Metric
R45, R46, R47, R48: 24.9k; R_0402_1005Metric
R53, R54: 82.5k; R_0603_1608Metric
R55, R57: 100R; R_0402_1005Metric
R56: 1R; R_0603_1608Metric
R58: 2k; R_0402_1005Metric
R59: 200; R_0402_1005Metric
R60: 4R; R_0603_1608Metric
R61, R62, R63, R64, R65, R66, R67, R68: 10R; R_0402_1005Metric
SW1: RESET; PTS815SJM250SMTRLFS
SW2: BOOT; PTS815SJM250SMTRLFS
TP1, TP4: TestPoint; TestPoint_Pad_1.0x1.0mm
TP2, TP3: TestPoint; TestPoint_Pad_4.0x4.0mm
U1: TMP117; Texas_DSBGA-6_0.95x1.488mm_Layout2x3_P0.4mm
U2: ESP32S2MINI1N4R2
U3: USB4105

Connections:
5v_Batt: C19.1, IC3.1 (SYS), J10.1
5v_Sel: C21.1, IC3.10 (IN), J5.2, J10.3
5v_Sys: C27.1, C34.1, IC6.3 (VIN), IC6.4 (EN), IC7.A1 (VDD), J10.2
5v_USB: C10.1, IC1.9 (AD), IC2.A2 (D1_1), IC2.A3 (D1_2), IC2.B3 (D1_3), J5.3, U3.2 (A4-B9), U3.11 (B4-A9)
5v_Wireless: C5.1, C6.1, IC1.4 (OUT), IC2.B2 (D2_1), IC2.C2 (D2_2), IC2.C3 (D2_3)
+3.3V: C3.1, C4.1, J4.1, J13.1, R1.1, R2.2, R3.2, R4.2, R11.1, R13.1, R14.1, R15.1, R62.2, U1.B1 (V+), U2.3 (3V3)
+3.3VA: C51.1, C52.1, C53.1, C54.1, C55.1, C56.1, C57.1, C58.1, C66.1, C67.1, C68.1, C82.1, C83.1, IC8.7 (+VS), IC9.7 (+VS), IC10.7 (+VS), IC11.7 (+VS), IC12.3 (EN), IC12.4 (VIN), IC13.4 (V+), IC16.7 (+VS), J14.1, R61.2
+3.3va: C30.1, C32.1, IC5.10 (OUTP), J14.2, R25.1
+3v: C26.1, J13.2, L1.1, R19.1
+9v: C23.1, C24.1, D1.1 (K), IC5.1 (INP), IC5.2 (EN), J11.1, R21.1
-3.3va: C28.2, C29.1, IC5.6 (OUTN), J15.2, R24.2
-3V3: C43.1, C44.1, C45.1, C46.1, C47.1, C48.1, C49.1, C50.1, C75.1, C76.1, IC8.4 (-VS), IC9.4 (-VS), IC10.4 (-VS), IC11.4 (-VS), IC16.4 (-VS), J15.1
-9v: C25.1, C33.1, D2.2 (A), IC5.5 (INN), IC7.C1 (DIS1), J12.1, R27.1
AC1: C7.1, C8.1, C9.2, C17.2, C18.1, IC1.2 (AC1)
AC2: C11.1, C12.1, C13.2, C18.2, IC1.19 (AC2), TP3.1
ADC_1: J19.3, U2.5 (IO1)
ADC_2: J18.3, U2.6 (IO2)
ADC_3: J20.3, U2.7 (IO3)
ADC_4: J21.3, U2.8 (IO4)
ADC_5: J22.2, U2.15 (IO11)
ALERT: R2.1, U1.C2 (ALERT)
BOOT: C2.2, SW2.1, U2.4 (IO0)
Batt+: J7.1, J8.2
Batt-: J7.2, J9.2
CHRG_STAT1: IC3.9 (STAT1), J1.12, R15.2
CHRG_STAT2: IC3.3 (STAT2), J1.14, R13.2
COIL+: C17.1, TP2.1
D+: U2.24 (IO20), U3.6 (A6), U3.8 (B6)
D-: U2.23 (IO19), U3.5 (B7), U3.7 (A7)
Fuel_Status: IC4.A1 (GPOUT), J1.8, R14.2
GND: C1.2, C2.1, C3.2, C4.2, C5.2, C6.2, C10.2, C14.2, C15.2, C16.2, C19.2, C20.2, C21.2, C22.2, C23.2, C24.2, C25.2, C26.2, C27.2, C29.2, C31.2, C32.2, C33.2, C34.2, C35.2, C36.2, C37.2, C38.2, C39.2, C40.2, C41.2, C42.2, C43.2, C44.2, C45.2, C46.2, C47.2, C48.2, C49.2, C50.2, C51.2, C52.2, C53.2, C54.2, C55.2, C56.2, C57.2, C58.2, C59.2, C60.2, C61.2, C62.2, C63.2, C64.2, C65.2, C66.2, C67.2, C68.2, C69.2, C70.2, C72.2, C73.2, C74.2, C75.2, C76.2, C77.2, C79.2, C80.2, C81.2, C82.2, C83.2, C84.2, C85.2, C86.2, C87.2, C88.2, C89.2, D3.2 (A), D4.2 (A), D5.2 (A), D6.2 (A), IC1.1 (PGND_1), IC1.10 (EN1), IC1.11 (EN2), IC1.20 (PGND_2), IC1.21 (EP), IC3.4 (~CE), IC3.5 (GND), IC3.11 (EP), IC4.B2 (VSS_1), IC4.C1 (VSS_2), IC5.4 (GND), IC5.11 (EP), IC6.1 (GND), IC7.A4 (GND), IC12.1 (GND_1), IC12.2 (GND_2), IC13.11 (V-), IC16.3 (+IN), IC17.1 (REFIN-), IC17.17 (DGND), IC17.20 (AGND), IC17.21 (EP), J4.4, J7.3 (SHIELD), J7.4 (SHIELD), J8.3, J9.3, J17.11, J17.12, L3.2, R6.2, R8.2, R9.1, R10.2, R12.2, R16.2, R17.2, R18.2, R20.2, R22.2, R26.2, R30.1, R32.1, R34.1, R36.1, R38.1, R40.1, R42.1, R44.1, R56.1, SW1.2, SW2.2, U1.B2 (GND), U1.C1 (ADD0), U2.1 (GND), U2.2 (GND), U2.30 (GND), U2.42 (GND), U2.43 (GND), U2.46 (GND), U2.47 (GND), U2.48 (GND), U2.49 (GND), U2.50 (GND), U2.51 (GND), U2.52 (GND), U2.53 (GND), U2.54 (GND), U2.55 (GND), U2.56 (GND), U2.57 (GND), U2.58 (GND), U2.59 (GND), U2.60 (GND), U2.61 (GND), U2.62 (GND), U2.63 (GND), U2.64 (GND), U2.65 (GND), U2.66, U2.67, U2.68, U2.69, U2.70, U2.71, U2.72, U2.73, U3.1 (A1-B12), U3.12 (B1-A12), U3.13 (GND)
GPIO5: J2.1, U2.9 (IO5)
GPIO6: J2.3, U2.10 (IO6)
GPIO7: J2.5, U2.11 (IO7)
GPIO8: J2.7, U2.12 (IO8)
GPIO9: J2.9, U2.13 (IO9)
GPIO10: J2.11, U2.14 (IO10)
GPIO12: J3.1, U2.16 (IO12)
GPIO13: J3.2, U2.17 (IO13)
GPIO14: J3.3, U2.18 (IO14)
GPIO15: J3.4, U2.19 (IO15)
GPIO16: J3.5, U2.20 (IO16)
GPIO33: J1.13, U2.28 (IO33)
GPIO34: J1.11, U2.29 (IO34)
GPIO35: J1.9, U2.31 (IO35)
GPIO36: J1.7, U2.32 (IO36)
GPIO37: J1.5, U2.33 (IO37)
GPIO38: J1.3, U2.34 (IO38)
GPIO45: J1.1, U2.41 (IO45)
HV_En: IC7.B3 (STB1), IC7.B4 (STB2), J1.10
Istim: IC16.6 (OUT), J22.1
MCLK: J2.2, R66.1
unnamed: D1.2 (A), IC7.A3 (LX2), L2.1
unnamed: D2.1 (K), IC7.B1 (LX1), L3.1
unnamed: C59.1, D3.1 (K), IC13.3 (IN1+), R49.1
unnamed: C60.1, D4.1 (K), IC13.5 (IN2+), R50.1
unnamed: C61.1, D5.1 (K), IC13.10 (IN3+), R51.1
unnamed: C62.1, D6.1 (K), IC13.12 (IN4+), R52.1
unnamed: C9.1, IC1.3 (BOOT1)
unnamed: C13.1, IC1.17 (BOOT2)
unnamed: C7.2, IC1.5 (CLAMP1)
unnamed: C12.2, IC1.16 (CLAMP2)
unnamed: C8.2, IC1.6 (COMM1)
unnamed: C11.2, IC1.15 (COMM2)
unnamed: IC1.14 (FOD), R5.2, R6.1, R7.1
unnamed: IC1.12 (ILIM), R5.1
unnamed: IC1.13 (TS/CTRL), R8.1
unnamed: IC2.B1 (SS), TP1.1
unnamed: IC3.7 (ILIM/VSET), R17.1
unnamed: IC3.8 (ISET), R18.1
unnamed: IC3.6 (TS/MR), R16.1
unnamed: IC4.B1 (BIN), R12.1
unnamed: C22.1, IC4.B3 (VDD)
unnamed: IC5.8 (BUF), R23.1
unnamed: C28.1, IC5.7 (FBN), R23.2, R24.1
unnamed: C30.2, IC5.9 (FBP), R25.2, R26.1
unnamed: IC5.3 (NR/SS), TP4.1
unnamed: IC6.5 (FB), R19.2, R20.1
unnamed: IC6.2 (SW), L1.2
unnamed: IC7.A2 (HS2L), L2.2
unnamed: IC7.C4 (INV2), R21.2, R22.1
unnamed: IC7.C3 (NON1), R27.2, R28.1
unnamed: C31.1, IC7.C2 (VREF), R28.2
unnamed: C35.1, IC8.3 (+IN), R29.1, R30.2
unnamed: C39.1, IC8.2 (-IN), R37.1, R38.2
unnamed: IC8.1 (RG_1), R45.2
unnamed: IC8.8 (RG_2), R45.1
unnamed: C36.1, IC9.3 (+IN), R31.1, R32.2
unnamed: C40.1, IC9.2 (-IN), R39.1, R40.2
unnamed: IC9.1 (RG_1), R46.2
unnamed: IC9.8 (RG_2), R46.1
unnamed: C37.1, IC10.3 (+IN), R33.1, R34.2
unnamed: C41.1, IC10.2 (-IN), R41.1, R42.2
unnamed: IC10.1 (RG_1), R47.2
unnamed: IC10.8 (RG_2), R47.1
unnamed: C38.1, IC11.3 (+IN), R35.1, R36.2
unnamed: C42.1, IC11.2 (-IN), R43.1, R44.2
unnamed: IC11.1 (RG_1), R48.2
unnamed: IC11.8 (RG_2), R48.1
unnamed: C63.1, IC12.5 (NR)
unnamed: IC14.3 (+IN1), R54.2, R57.1
unnamed: C78.2, IC14.5 (+IN2), R60.2
unnamed: C71.1, IC14.2 (-IN1), R53.2, R55.1
unnamed: IC14.6 (-IN2), IC14.7 (VOUT2), R57.2
unnamed: C71.2, IC14.1 (VOUT1), IC15.3 (+IN)
unnamed: IC15.4 (-IN), R58.2
unnamed: IC15.1 (VOUT), R55.2, R58.1, R60.1
unnamed: IC16.1 (RG_1), R59.2
unnamed: IC16.8 (RG_2), R59.1
unnamed: C86.1, C87.1, IC17.19 (AVDD), R61.1
unnamed: C88.1, C89.1, IC17.18 (DVDD), R62.1
unnamed: IC17.16 (MCLK), R66.2
unnamed: IC17.12 (SCK), R68.2
unnamed: IC17.13 (SDI), R64.2
unnamed: IC17.14 (SDO), R67.2
unnamed: IC17.11 (~CS), R65.2
unnamed: IC17.15 (~IRQ/MDAT), R63.2
unnamed: R9.2, U3.4 (A5)
unnamed: R10.1, U3.10 (B5)
OADC_1: IC17.3 (CH0), J19.1
OADC_2: IC17.4 (CH1), J18.1
OADC_3: IC17.5 (CH2), J20.1
OADC_4: IC17.6 (CH3), J21.1
OUT_SEL: IC1.8 (~AD-EN), IC2.A1 (G1), IC2.C1 (G2), J5.1
P_1: IC13.1 (OUT1), IC13.2 (IN1-), J19.2
P_2: IC13.6 (IN2-), IC13.7 (OUT2), J18.2
P_3: IC13.8 (OUT3), IC13.9 (IN3-), J20.2
P_4: IC13.13 (IN4-), IC13.14 (OUT4), J21.2
Probe_1: IC8.6 (OUT), R49.2
Probe_2: IC9.6 (OUT), R50.2
Probe_3: IC10.6 (OUT), R51.2
Probe_4: IC11.6 (OUT), R52.2
Probe_in_1+: J16.2, J17.2, R29.2
Probe_in_1-: J16.1, J17.1, R37.2
Probe_in_2+: J16.4, J17.4, R31.2
Probe_in_2-: J16.3, J17.3, R39.2
Probe_in_3+: J16.6, J17.6, R33.2
Probe_in_3-: J16.5, J17.5, R41.2
Probe_in_4+: J16.8, J17.8, R35.2
Probe_in_4-: J16.7, J17.7, R43.2
RECT: C14.1, C15.1, C16.1, IC1.18 (RECT), R7.2
RESET: C1.1, R1.2, SW1.1, U2.45 (EN)
RX: J4.2, U2.40 (RXD0)
SCK: J2.10, R68.1
SCL: IC4.A3 (SCL), J1.4, R3.1, U1.A2 (SCL)
SDA: IC4.A2 (SDA), J1.6, R4.1, U1.A1 (SDA)
SDI: J2.8, R64.1
SDO: J2.6, R67.1
Stim+: C77.1, C79.1, C80.1, C81.1, IC14.8 (+VS), IC15.5 (+VS), J11.2
Stim-: C69.1, C70.1, C72.1, C73.1, IC14.4 (-VS), IC14.9 (EP), IC15.2 (-VS), J12.2
Stim_control+: R53.1, U2.22 (IO18)
Stim_control-: R54.1, U2.21 (IO17)
Stim_gnd: C74.1, IC16.2 (-IN), J16.10, J17.10, R56.2
Stim_out: C78.1, J16.9, J17.9
TX: J4.3, U2.39 (TXD0)
V_Batt: C20.1, IC4.C3 (BAT), J6.2, J8.1, J9.1
V_Fuel: IC3.2 (BAT), IC4.C2 (SRX), J6.1
Vref: C64.1, C65.1, C84.1, C85.1, IC8.5 (REF), IC9.5 (REF), IC10.5 (REF), IC11.5 (REF), IC12.6 (VREF), IC16.5 (REF), IC17.2 (REFIN+/OUT)
Wireless_Status: IC1.7 (~CHG), J1.2, R11.2
~CS: J2.12, R65.1
~IRQ: J2.4, R63.1

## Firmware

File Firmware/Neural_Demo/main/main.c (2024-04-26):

#include <stdio.h>
#include "esp_log.h"
#include "esp_check.h"
#include "driver/gpio.h"
#include "freertos/FreeRTOS.h"
#include "freertos/task.h"
#include "freertos/queue.h"

#include "esp_adc/adc_oneshot.h"
#include "esp_adc/adc_cali.h"
#include "esp_adc/adc_cali_scheme.h"

// Local includes
#include "tmp117.h"
#include "mcp3464.h"
#include "wifi.h"
#include "udp.h"

//****************Pin Definitions*******************

#define ADC_1   1
#define ADC_2   2
#define ADC_3   3
#define ADC_4   4
#define ADC_5   11

#define STIM_P  17
#define STIM_N  18

#define WIRELESS_STATUS 45
#define FUEL_STATUS     36
#define HIGH_VOLTAGE_EN 35
#define CHARGE_STAT_1   34
#define CHARGE_STAT_2   33

#define I2C_SCL 38
#define I2C_SDA 37

#define MCP3464_MCLK    5
#define MCP3464_IRQ     6
#define MCP3464_SDO     7
#define MCP3464_SDI     8
#define MCP3464_SCK     9
#define MCP3464_CS      10


//****************Other Definitions*******************

// I2C
#define PORT_NUMBER -1
#define I2C_CLK_FREQ 400000    

// SPI
#define SPI_ADC_HOST 1
#define SPI_CLK_FREQ 20000000

// MCP3464
#define MCP3464_CHANNEL_0       0b0000
#define MCP3464_CHANNEL_1       0b0001
#define MCP3464_CHANNEL_2       0b0010
#define MCP3464_CHANNEL_3       0b0011

// How many readings are averaged for every adc value
#define AVERAGING   32

// Transmission parameters
#define PAYLOAD_LENGTH      405 
#define PAYLOAD_SAMPLES     200

static const char *TAG = "MAIN";

static char payload[PAYLOAD_LENGTH];


void app_main(void)
{

    // Initialize the nvs flash (used for wifi)
    esp_err_t ret = nvs_flash_init();
    if(ret == ESP_ERR_NVS_NO_FREE_PAGES || ret == ESP_ERR_NVS_NEW_VERSION_FOUND){
        ESP_ERROR_CHECK(nvs_flash_erase());
        ret = nvs_flash_init();
    }

    ESP_ERROR_CHECK(ret);

    // Initialize wifi
    wifiInit();

    // Make sure current output is set to zero by default
    gpio_reset_pin(STIM_P);
    gpio_set_direction(STIM_P, GPIO_MODE_OUTPUT);
    gpio_set_level(STIM_P, 0);

    gpio_reset_pin(STIM_N);
    gpio_set_direction(STIM_N, GPIO_MODE_OUTPUT);
    gpio_set_level(STIM_N, 0);

    // Turn on high voltage supply
    gpio_reset_pin(HIGH_VOLTAGE_EN);
    gpio_set_direction(HIGH_VOLTAGE_EN, GPIO_MODE_OUTPUT);
    gpio_set_level(HIGH_VOLTAGE_EN, 1);    


    // Initialize SPI bus
    ESP_LOGI(TAG, "Initializing bus SPI%d...", SPI_ADC_HOST + 1);

    spi_bus_config_t buscfg = {
        .miso_io_num = MCP3464_SDO,
        .mosi_io_num = MCP3464_SDI,
        .sclk_io_num = MCP3464_SCK,
        .quadwp_io_num = -1,
        .quadhd_io_num = -1,
        .max_transfer_sz = 32,
    };

    ESP_ERROR_CHECK(spi_bus_initialize(SPI_ADC_HOST, &buscfg, SPI_DMA_CH_AUTO));

    // Initialize ADC
    mcp3464_conf_t mcp3464_conf = {
        .cs_io = MCP3464_CS,
        .host = SPI_ADC_HOST,
        .miso_io = MCP3464_SDO,
        .clock_speed_hz = SPI_CLK_FREQ,
    };

    mcp3464_handle_t mcp3464_handle;

    ESP_ERROR_CHECK(mcp3464_init(&mcp3464_conf, &mcp3464_handle));


    // Configure I2C
    i2c_master_bus_config_t i2c_bus_config = {
        .clk_source = I2C_CLK_SRC_DEFAULT,
        .i2c_port = PORT_NUMBER,
        .scl_io_num = I2C_SCL,
        .sda_io_num = I2C_SDA,
        .glitch_ignore_cnt = 7,
    };
    i2c_master_bus_handle_t bus_handle;
    ESP_ERROR_CHECK(i2c_new_master_bus(&i2c_bus_config, &bus_handle));


    // Configure the TMP117
    tmp117_conf_t tmp117_conf = {
        .addr = TMP117_DEFAULT_ADDR,
        .alert_mode = 0,
        .alert_polarity = 0,
        .averaging = 8,
        .conversion_period = 125,
        .dr_al_select = 0,
        .mode = 0,
        .scl_speed_hz = I2C_CLK_FREQ,
        .timeout_ms = -1,
    };
    tmp117_handle_t tmp117_handle;
    int conversion_rate;
    ESP_ERROR_CHECK(tmp117_init(bus_handle, &tmp117_conf, &tmp117_handle, &conversion_rate));
    ESP_LOGI(TAG, "tmp117 conversion rate: %d", conversion_rate);
    uint16_t current_temperature;
    

    // Configure the onboard ADC
    adc_oneshot_unit_handle_t adc2_handle;
    adc_oneshot_unit_init_cfg_t init_config2 = {
        .unit_id = ADC_UNIT_2,
        .ulp_mode = ADC_ULP_MODE_DISABLE,
    };

    ESP_ERROR_CHECK(adc_oneshot_new_unit(&init_config2, &adc2_handle));
    adc_oneshot_chan_cfg_t config = {
        .bitwidth = ADC_BITWIDTH_DEFAULT,
        .atten = ADC_ATTEN_DB_12,        // makes it possible to measure values larger than vref
    };
    ESP_ERROR_CHECK(adc_oneshot_config_channel(adc2_handle, ADC_CHANNEL_0, &config));

    // Calibrate the onboard ADC
    adc_cali_handle_t adc2_cali_chan0_handle = NULL;
    adc_cali_line_fitting_config_t cali_config_2 = {
        .unit_id = ADC_UNIT_2,
        .atten = ADC_ATTEN_DB_12,
        .bitwidth = ADC_BITWIDTH_DEFAULT,
    };
    adc_cali_create_scheme_line_fitting(&cali_config_2, &adc2_cali_chan0_handle); 
    

    uint32_t adc_val;  

    // Start first conversion, interrupt starts conversions afterwards
    mcp3464_start_conversion(mcp3464_handle);

    // Create the task to revieve messages over UDP
    xTaskCreate(udp_recieve_task, "udp_client", 4096, NULL, 5, NULL);

    while(1){

        // Set the start byte of the payload
        payload[0] = 'S';

        int samples = 0;
        int channel_0_samples = 0;
        int channel_1_samples = 0;
        int channel_2_samples = 0;
        int channel_3_samples = 0;
        int channel_4_samples = 0;

        int adc_val;
        int adc_onboard_val = 0;

        int adc_val_cal = 0;


        while(samples < PAYLOAD_SAMPLES){
            if(xQueueReceive(mcp3464_handle->irq_queue, &adc_val, portMAX_DELAY)){
                uint8_t channel = (adc_val >> 24) & 0b1111;
                


                if((samples == 0) && (channel != MCP3464_CHANNEL_0)){
                    channel = 200;
                }

                switch(channel){
                    case MCP3464_CHANNEL_0:
                        ESP_LOGI(TAG,"ADC channel 0 Reading: %d", (uint16_t)(adc_val & 0b1111111111111111));
                        payload[3 + (channel_0_samples * 2)]      = adc_val >> 8;
                        payload[3 + (channel_0_samples * 2) + 1]  = adc_val;
                        channel_0_samples += 1;
                        samples += 1;
                        break;
                    case MCP3464_CHANNEL_1:
                        payload[3 + (PAYLOAD_SAMPLES * 2 / 5) + (channel_1_samples * 2)]      = adc_val >> 8;
                        payload[3 + (PAYLOAD_SAMPLES * 2 / 5) + (channel_1_samples * 2) + 1]  = adc_val;
                        channel_1_samples += 1;
                        samples += 1;
                        break;
                    case MCP3464_CHANNEL_2:
                        payload[3 + 2 * (PAYLOAD_SAMPLES * 2 / 5) + (channel_2_samples * 2)]      = adc_val >> 8;
                        payload[3 + 2 * (PAYLOAD_SAMPLES * 2 / 5) + (channel_2_samples * 2) + 1]  = adc_val;
                        channel_2_samples += 1;
                        samples += 1;
                        break;
                    case MCP3464_CHANNEL_3:
                        
                        payload[3 + 3 * (PAYLOAD_SAMPLES * 2 / 5) + (channel_3_samples * 2)]      = adc_val >> 8;
                        payload[3 + 3 * (PAYLOAD_SAMPLES * 2 / 5) + (channel_3_samples * 2) + 1]  = adc_val;
                        channel_3_samples += 1;
                        samples += 1;

                        // Do onboard adc reading
                        uint32_t adc_val_4 = 0;

                        // Average the ADC readings
                        for(int i = 0; i < AVERAGING; i++){

                            adc_oneshot_read(adc2_handle, ADC_CHANNEL_0, &adc_onboard_val);
                            ESP_ERROR_CHECK(adc_cali_raw_to_voltage(adc2_cali_chan0_handle, adc_onboard_val, &adc_val_cal));
                            adc_val_4 += adc_val_cal;
                
                        }

                        // Divide the ADC readings by 32
                        adc_val_4 = adc_val_4 >> 5;

                        payload[3 + 4 * (PAYLOAD_SAMPLES * 2 / 5) + (channel_4_samples * 2)]      = adc_val_4 >> 8;
                        payload[3 + 4 * (PAYLOAD_SAMPLES * 2 / 5) + (channel_4_samples * 2) + 1]  = adc_val_4;
                        channel_4_samples += 1;
                        samples += 1;

                        break;
                    default:
                        ESP_LOGE(TAG,"Unexpected ADC channel");
                }

                
            }
     
    
        }

        // Add stop bytes to payload (used for debugging)
        payload[PAYLOAD_LENGTH - 2] =  '\r';
        payload[PAYLOAD_LENGTH - 1] =  '\n';

        // Read the temperature
        ESP_ERROR_CHECK_WITHOUT_ABORT(tmp117_read_temp_raw_blocking(tmp117_handle, &current_temperature));
        ESP_LOGI(TAG, "temperature = %d", tmp117_convert_to_c(current_temperature));
        ESP_LOGI(TAG, "ESP ADC VAL: %d", adc_val);
        
        // Write the temperature to the payload
        payload[1] = current_temperature >> 8;
        payload[2] = current_temperature;

        // Transmit the payload
        xTaskCreate(udp_client_task, "udp_client", 4096, &payload, 5, NULL); 


    }


}

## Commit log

2024-03-21 Add ESP32 to design
    [Analog_Frontend.kicad_sch, Neural_Interface.kicad_pcb, Neural_Interface.kicad_sch, Power_Manegement.kicad_sch]
2024-03-21 Reorganize files
    [Analog_Frontend.kicad_sch, Neural_Interface.kicad_pcb, Neural_Interface.kicad_sch, Power_Manegement.kicad_sch]
2024-03-25 Add charging circuitry
    Warning Voltage dividers for switching regulator not speced correctly!!
    [Power_Manegement.kicad_sch]
2024-03-26 Power Management Complete
    [Neural_Interface.kicad_sch, Power_Manegement.kicad_sch]
2024-03-27 Design Analog Frontend
    [Analog_Frontend.kicad_sch, Neural_Interface.kicad_sch, Power_Manegement.kicad_sch]
2024-03-27 Add Current Measurement
    [Analog_Frontend.kicad_sch]
2024-03-29 Spec all components
    [Analog_Frontend.kicad_sch, Neural_Interface.kicad_sch, Power_Manegement.kicad_sch]
2024-04-01 Start Layout
    [Analog_Frontend.kicad_sch, Neural_Interface.kicad_pcb, Neural_Interface.kicad_sch, Power_Manegement.kicad_sch]
2024-04-02 Completed Layout
    [Neural_Interface-B_Cu.gbr, Neural_Interface-B_Mask.gbr, Neural_Interface-B_Paste.gbr, Neural_Interface-B_Silkscreen.gbr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]
2024-04-03 Create ESP project
    [Neural_Interface.kicad_pcb]
2024-04-04 Add code to read temperature sensor
    This code compiles but has not been tested on hardware yet, this was largely based on a previous implementation I wrote for a different MCU
2024-04-13 temperature sensor working
2024-04-23 Analog measurement demo working
    The device will connect to wifi and transmit its readings from channel one, as well as the temperature.
2024-04-24 Single Channel Demo with current stimulation
    Can now receive data over UDP and create a sine wave or square wave with arbitrary amplitude from received data.
    Matlab demo is now made using UI elements to make it possible to send commands to the device using a dropdown menu to select the wave and a slider to select the amplitude.
2024-04-25 onboard ADC demo working
    current sensing not added yet
2024-04-25 current measurement working
    still using the onboard adc
2024-04-25 Rename Neural_Interface-Power Manegement.svg to Neural_Interface-Power_Manegement.svg
    remove space
2024-04-26 add manufacturing files
    [BOM.csv, DigiKeyPartsOrder.xlsx, MouserPartsOrder.xls]
2024-05-02 Remove personal logo
    The project will be made open source, but the logo will not fall under that license so I am removing it.
    [Neural_Interface-B_Cu.gbr, Neural_Interface-B_Mask.gbr, Neural_Interface-B_Paste.gbr, Neural_Interface-B_Silkscreen.gbr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]
